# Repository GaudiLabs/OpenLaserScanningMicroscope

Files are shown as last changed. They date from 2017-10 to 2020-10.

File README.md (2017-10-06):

## OpenLaserScanningMicroscope 

Open Source Laser Scanning Microscope (OpenLSM)

### Don't click on the files!
Click on the "Download ZIP" Button to the right.
Then unpack the archive.

### Open Source Digital Microfluidics Bio Lab

OpenLSM is an open source design to build a laser scanning microscope from a DVD or Blue-Ray disc reading head. 

For more info on the open source project see:
http://www.gaudi.ch/GaudiLabs/?page_id=652

### License

OpenLSM, all design files and software are licensed under a GNU GENERAL PUBLIC LICENSE
See license file in the repository.

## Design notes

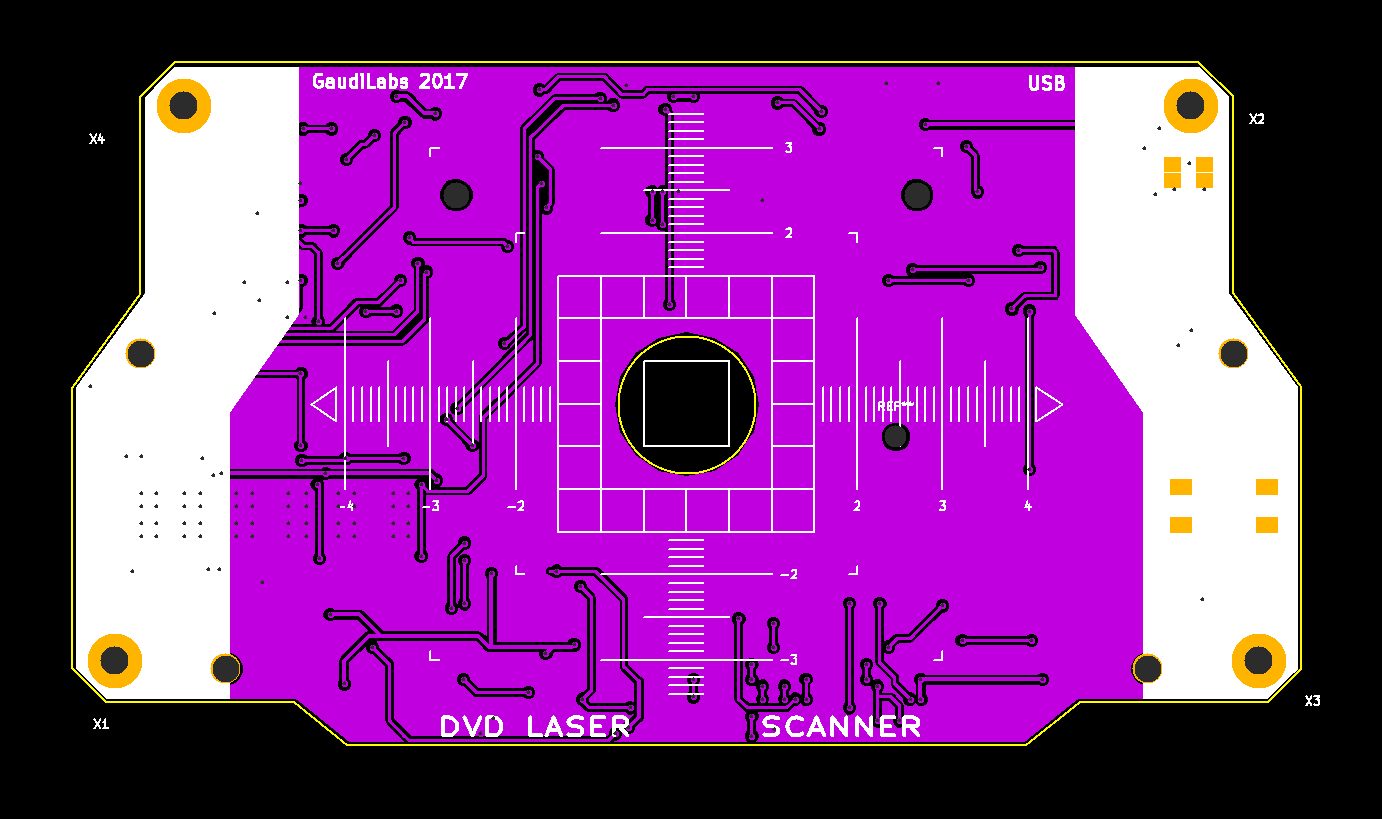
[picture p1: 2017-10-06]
PCB/DVDLaserScannerII/Pictures/DVDScannerII_Front.png

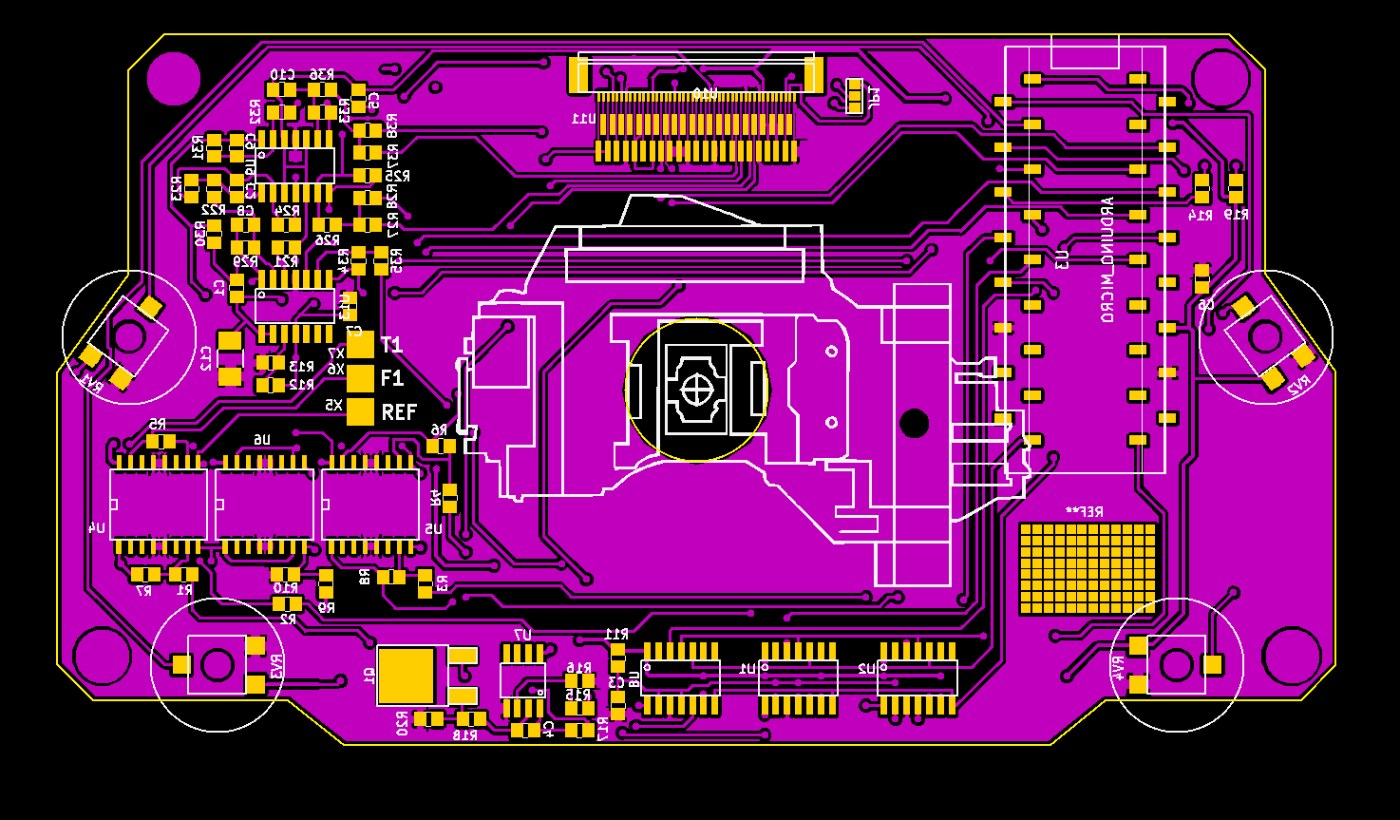
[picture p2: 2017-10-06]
PCB/DVDLaserScannerII/Pictures/DVDScanII.png

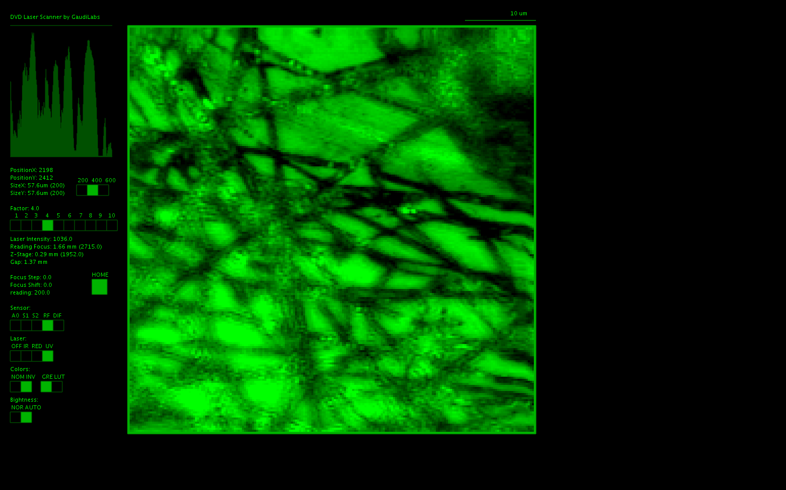
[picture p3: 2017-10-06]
ProcessingCode/DVDLaserV2_Inter/dump/LaserDump 2017-10-05 10:50:20.png

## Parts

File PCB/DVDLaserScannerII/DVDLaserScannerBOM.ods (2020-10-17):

Bill of Materials (BOM) DVD Laser Scanner V2
21. Juni 2017, Urs Gaudenz
Id | Quantity | Designator | Package | Order No | Designation | Quantity
26 | 3 | U4,U5,U6 | SO-16-W | 863-TCA0372DWG | TCA0372_DWG | 3
22 | 1 | U7 | SOIC-08_N |  | MCP6002 | 1
4 | 3 | U1,U2,U8 | SOIC-14_N |  | MCP4922-E/SL | 3
37 | 2 | U9,U13 | SOIC-14_N | 579-MCP6004-I/SL | MCP6004 | 2 | TLC2274
16 | 1 | Q1 | TO-252-2Lead | Q_NMOS_GDS | LR120N | 1
29 | 2 | C1,C8 | 0805G |  | 22pF | 2
30 | 2 | C2,C9 | 0805G | 33pF | 39pF | 2
7 | 1 | C3 | 0805G |  | 100nF | 1
14 | 3 | C4,C6,C7 | 0805G |  | 100nF | 3
31 | 2 | C5,C10 | 0805G |  | 10pF | 2
36 | 1 | C12 | C_1210_HandSoldering | ? 220 | 100nF | 1 |  | 470pF
15 | 2 | D1,D2 | 0805G |  | LED | 2 |  | 10pF
 |  | R2,R4, |  |  | 270k |  |  | 68pF
8 | 4 | R1,R3,R5,R6 | 0805G |  | 15k | 4 |  | 1nF
12 | 1 | R11 | 0805G |  | 100k | 1 |  | 2.2nF
13 | 1 | R13 | 0805G |  | 3.3k | 1 |  | 6.8nF
17 | 2 | R14,R19 | 0805G |  | 560 | 2 |  | 220nF
18 | 1 | R16 | 0805G |  | 1.8k | 1
19 | 1 | R17 | 0805G |  | 100 | 1 |  | 68Ohm
20 | 3 | R18,R22,R30 | 0805G |  | 10k | 3 |  | 8.2k
9 | 4 | R26,R36 | 0805G |  | 56k | 4 |  | 15k
21 | 1 | R20 | 0805G |  | 10 | 1 |  | 150k
25 | 2 | R21,R29 | 0805G |  | 39k | 2 |  | 180k
32 | 2 | R23,R31 | 0805G |  | 220k | 2 |  | 220k
33 | 2 | R24,R32 | 0805G |  | 68k | 2
34 | 2 | R25,R33 | 0805G |  | 18k | 2
35 | 4 | R27,R28,R37,R38 | 0805G |  | 1.2k | 4
10 | 3 | R7,R8,R15 | 0805G |  | 8.2k | 3
11 | 3 | R9,R10,R12 | 0805G |  | 4.7k | 5
 | 1 | R34 |  |  | 560k
 | 1 | R35 |  |  | 2.7k
5 | 1 | U3 | ARDUINO_MICRO_SMD |  | ARDUINO_MICRO | 1
3 | 4 | RV4,RV3,RV2,RV1 | CA6_VSMD | CA6 Carbon Potentiometers CA | ACP 6-SMD 10K | 4
3 |  |  |  | Poti Pins
2 | 1 | U11 | FFC_05_45 | 798-FH12A-45S0.5SH55 | Con45 | 1
 | 1 |  | FCC Cable | 710-687645152002 |  | 1
28 | 1 | SW1 | PUSH_BUTTON_SMD |  | BUT | 1
 | 2 |  | DVD Head | ebay | PHR-803T | 2
 | 1 |  | Mounting Brackets |  |  | 1
 | 1 |  | Mounting Brackets |  |  | 1
 | 4 |  | Spacers |  |  | 4

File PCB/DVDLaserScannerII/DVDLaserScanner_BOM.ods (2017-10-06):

Id | Designator | Package | Quantity | Designation | Supplier and ref
2 | U1,U2,U8 | SOIC-14_N | 3 | MCP4922-E/SL
4 | U3 | ARDUINO_MICRO_SMD | 1 | ARDUINO_MICRO
5 | X1,X2,X3,X4 | MountingHoleM3 | 4 | MountPad3 |  | reichelt
6 | C1,C2 | FFC_05_24 | 2 | SF-HF65
7 | REF** | HeatSink19x13 | 1 | HeatSink19x13 |  | reichelt
8 | U4,U5,U6 | SOIC-08_N | 3 | TCA0372 | mouser
9 | C3 | 0805G | 1 | 100nF
10 | R1,R3,R5,R6 | 0805G | 4 | 15k
11 | R2,R4 | 0805G | 2 | 56k
12 | R7,R8,R15 | 0805G | 3 | 8.2k
13 | R9,R10,R12 | 0805G | 3 | 4.7k
14 | R11 | 0805G | 1 | 100k
15 | R13 | 0805G | 1 | 3.3k
16 | C4 | 0805G | 1 | 100n | 1nF?
17 | D1,D2 | 0805G | 2 | LED
18 | Q1 | TO-252-2Lead | 1 | Q_NMOS_GDS
19 | R14,R19 | 0805G | 2 | 470
20 | R16 | 0805G | 1 | 1.8k
21 | R17 | 0805G | 1 | 100
22 | R18 | 0805G | 1 | 10k
23 | R20 | 0805G | 1 | 10
24 | U7 | SOIC-08_N | 1 | MCP6002
25 | U9 | Pads_24 | 1 | Con24 | mouser
26 | U11 | FFC_05_45 | 1 | Con45 | mouser
27 | U10 | Pads | 1 | Con45 | mouser
30 | R21 | 0805G | 1 | 2.2k
31 | RV4,RV3,RV2,RV1 | CA6_VSMD | 4 | POT |  | reichelt

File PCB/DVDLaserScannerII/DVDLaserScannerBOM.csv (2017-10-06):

Id | Designator | Package | Quantity | Designation | Supplier and ref
1 | REF** | MicroscopeyScale | 1 | MicroscopeyScale
2 | U11 | FFC_05_45 | 1 | Con45
3 | RV4,RV3,RV2,RV1 | CA6_VSMD | 4 | POT
4 | U1,U2,U8 | SOIC-14_N | 3 | MCP4922-E/SL
5 | U3 | ARDUINO_MICRO_SMD | 1 | ARDUINO_MICRO
6 | X1,X2,X3,X4 | MountingHoleM3 | 4 | MountPad3
7 | C3 | 0805G | 1 | 100nF
8 | R1,R3,R5,R6 | 0805G | 4 | 15k
9 | R2,R4,R26,R36 | 0805G | 4 | 56k
10 | R7,R8,R15 | 0805G | 3 | 8.2k
11 | R9,R10,R12,R34,R35 | 0805G | 5 | 4.7k
12 | R11 | 0805G | 1 | 100k
13 | R13 | 0805G | 1 | 3.3k
14 | C4,C6,C7 | 0805G | 3 | 100n
15 | D1,D2 | 0805G | 2 | LED
16 | Q1 | TO-252-2Lead | 1 | Q_NMOS_GDS
17 | R14,R19 | 0805G | 2 | 470
18 | R16 | 0805G | 1 | 1.8k
19 | R17 | 0805G | 1 | 100
20 | R18,R22,R30 | 0805G | 3 | 10k
21 | R20 | 0805G | 1 | 10
22 | U7 | SOIC-08_N | 1 | MCP6002
23 | REF**,REF** | MountingHole_3mm | 2 | MountingHole_3mm
24 | JP1 | GS3 | 1 | Jumper_NC_Dual
25 | R21,R29 | 0805G | 2 | 39k
26 | U4,U5,U6 | SO-16-W | 3 | TCA0372_DWG
27 | U10 | Pads | 1 | Con45
28 | SW1 | PUSH_BUTTON_SMD | 1 | BUT
29 | C1,C8 | 0805G | 2 | 22pF
30 | C2,C9 | 0805G | 2 | 39pF
31 | C5,C10 | 0805G | 2 | 10pF
32 | R23,R31 | 0805G | 2 | 180k
33 | R24,R32 | 0805G | 2 | 68k
34 | R25,R33 | 0805G | 2 | 18k
35 | R27,R28,R37,R38 | 0805G | 4 | 1.2k
36 | C12 | C_1210_HandSoldering | 1 | CP_Small
37 | U9,U13 | SOIC-14_N | 2 | TLC2274
38 | G*** | PHR-803T | 1 | LOGO
39 | X5,X6,X7 | PAD_SMD_3mm | 3 | PAD
40 | REF** | MountingHole_2-5mm | 1 | MountingHole_2-5mm
41 | REF** | SMD_Array | 1 | SMD_Array

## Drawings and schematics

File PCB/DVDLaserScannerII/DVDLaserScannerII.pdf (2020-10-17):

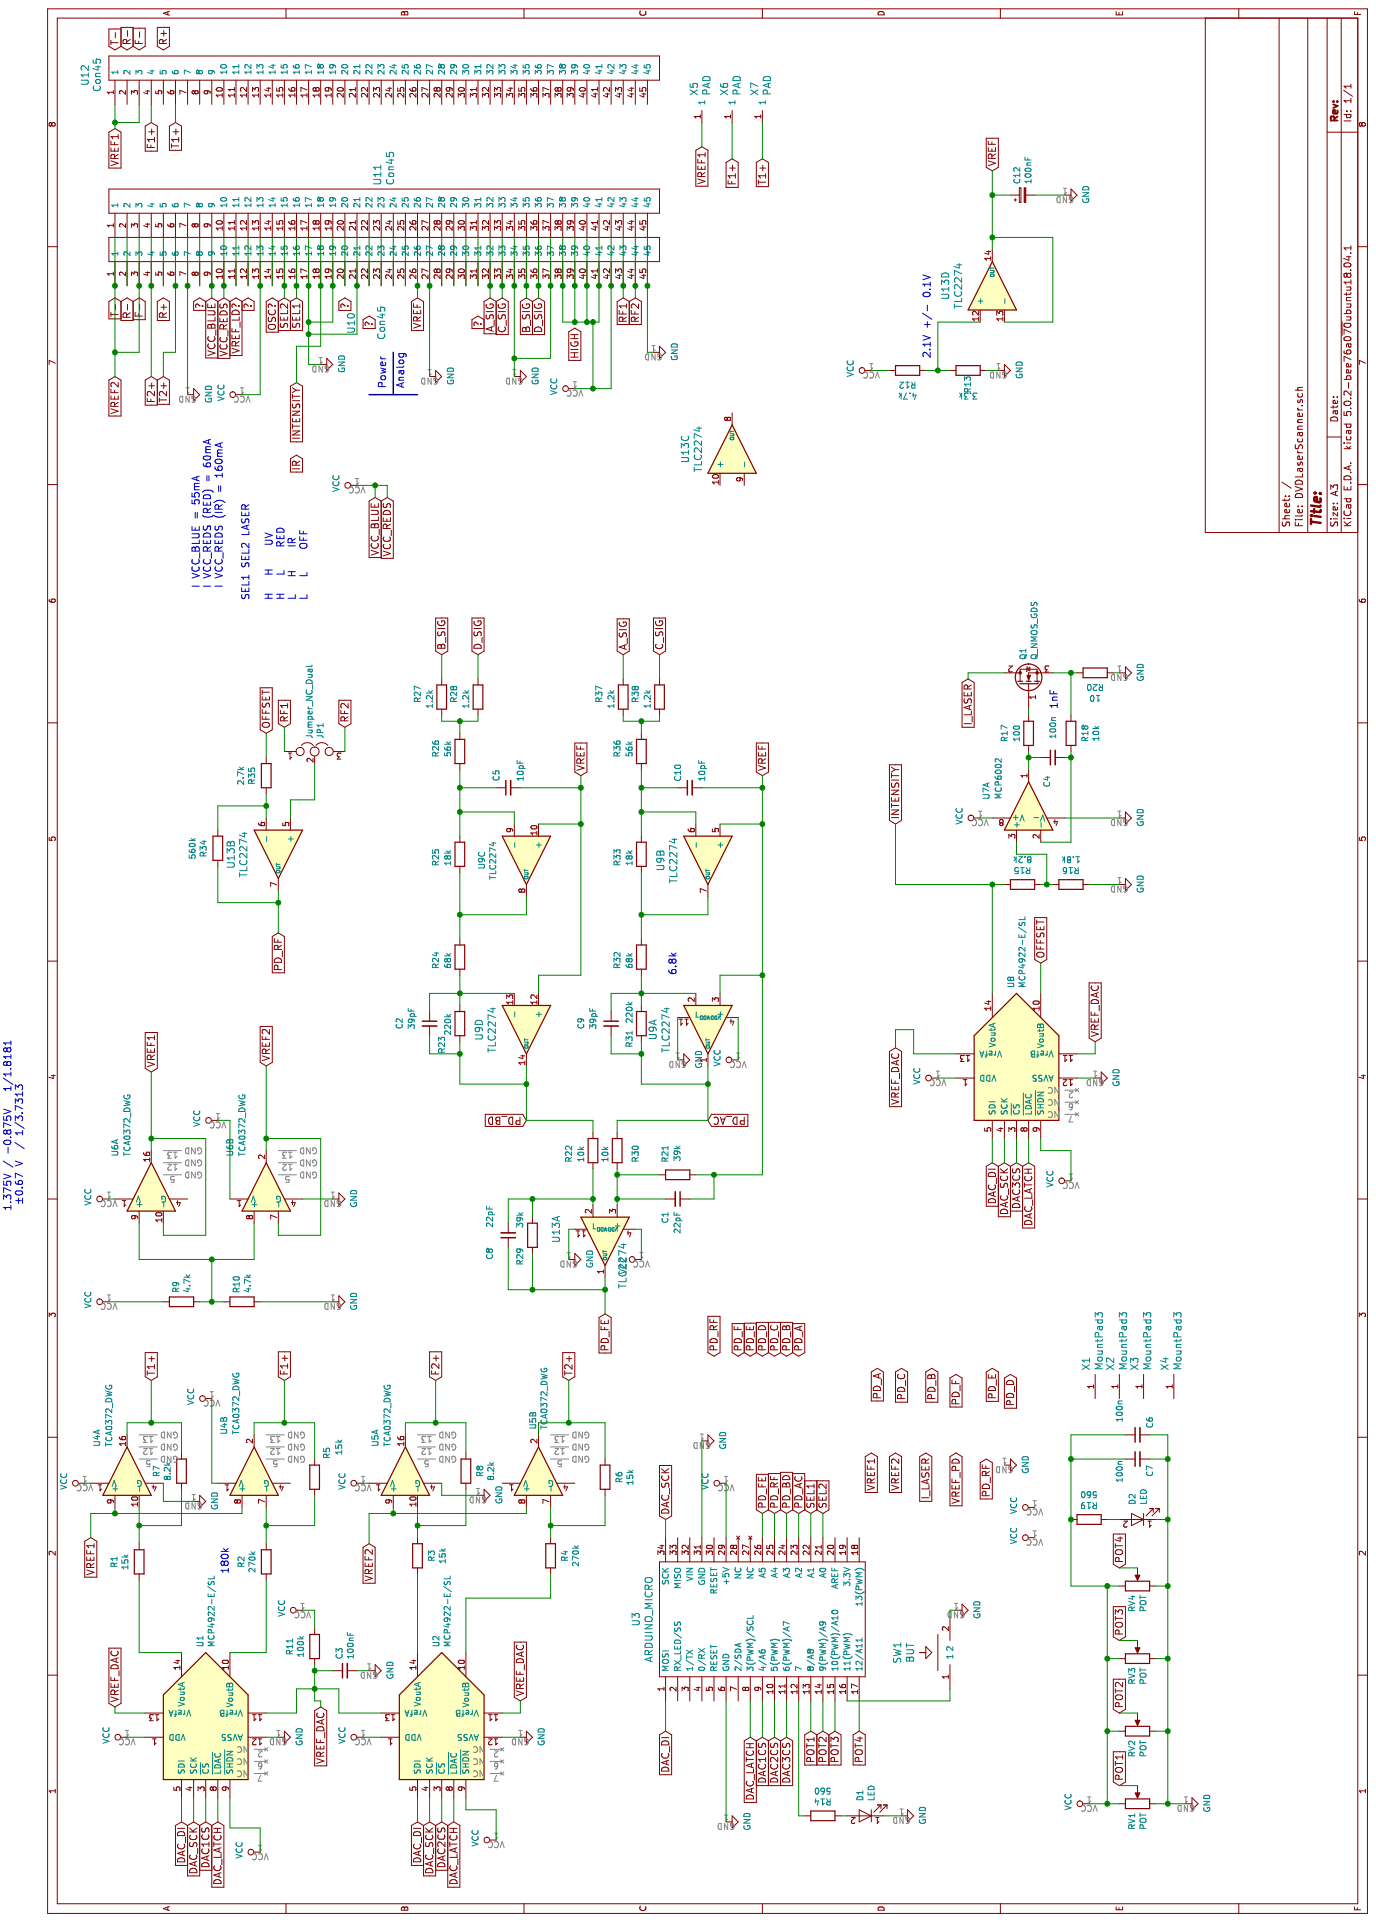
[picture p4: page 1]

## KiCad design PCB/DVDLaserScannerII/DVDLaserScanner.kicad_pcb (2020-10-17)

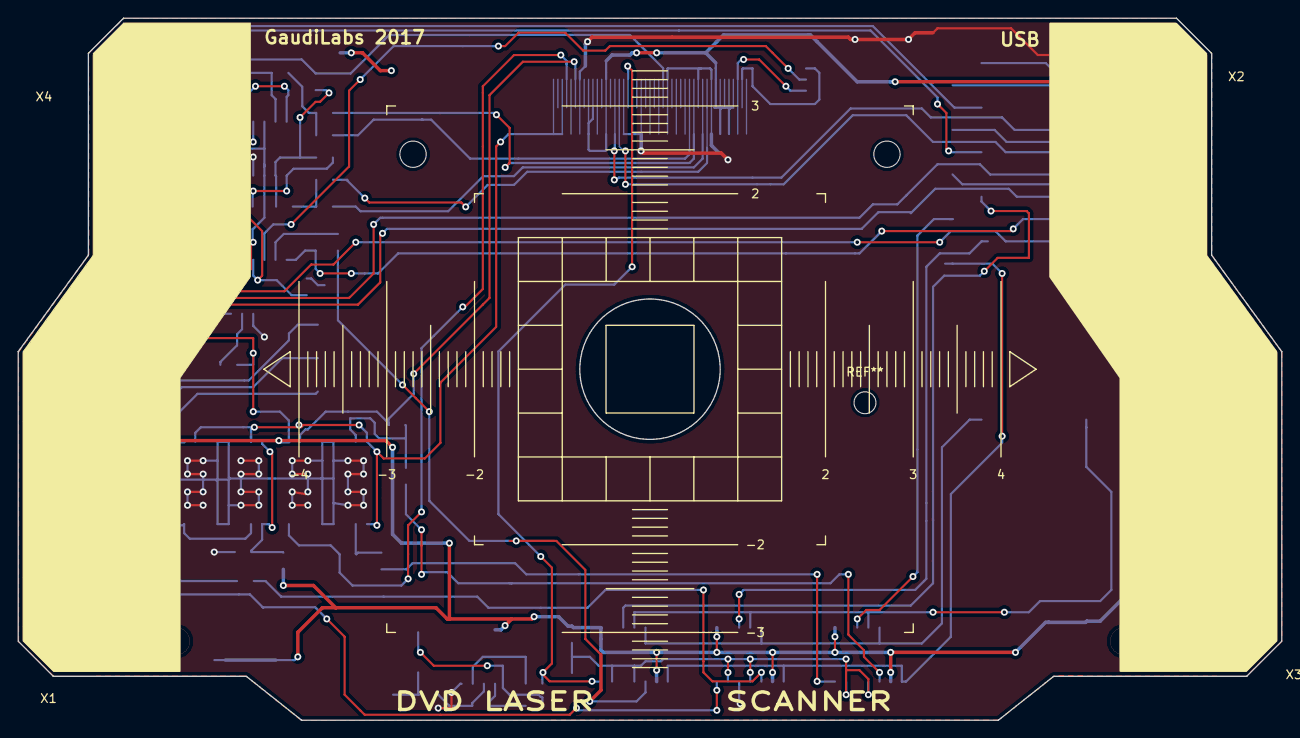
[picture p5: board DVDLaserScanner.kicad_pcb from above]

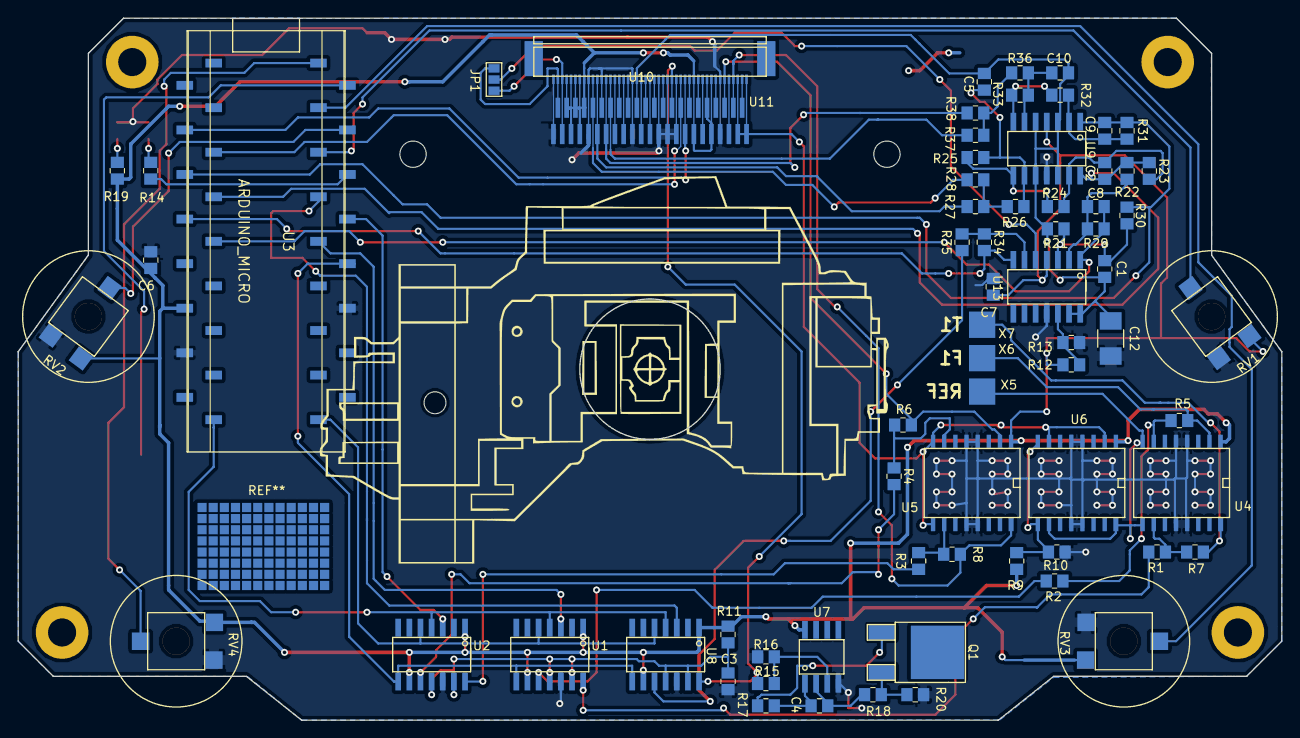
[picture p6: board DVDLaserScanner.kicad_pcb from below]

Board: 2 copper layers, 144.0 x 80.0 mm, 77 parts (70 on the bottom side), 80 nets.

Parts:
C1, C8: 22pF; 0805G
C2, C9: 39pF; 0805G
C3: 100nF; 0805G
C4, C6, C7: 100n; 0805G
C5, C10: 10pF; 0805G
C12: 100nF; C_1210_HandSoldering
D1, D2: LED; 0805G
JP1: Jumper_NC_Dual; GS3
Q1: Q_NMOS_GDS; TO-252-2Lead
R1, R3, R5, R6: 15k; 0805G
R2, R4: 270k; 0805G
R7, R8, R15: 8.2k; 0805G
R9, R10, R12: 4.7k; 0805G
R11: 100k; 0805G
R13: 3.3k; 0805G
R14, R19: 470; 0805G
R16: 1.8k; 0805G
R17: 100; 0805G
R18, R22, R30: 10k; 0805G
R20: 10; 0805G
R21, R29: 39k; 0805G
R23, R31: 180k; 0805G
R24, R32: 68k; 0805G
R25, R33: 18k; 0805G
R26, R36: 56k; 0805G
R27, R28, R37, R38: 1.2k; 0805G
R34: 560k; 0805G
R35: 2.7k; 0805G
RV1, RV2, RV3, RV4: POT; CA6_VSMD
SW1: BUT; PUSH_BUTTON_SMD
U1, U2, U8: MCP4922-E/SL; SOIC-14_N
U3: ARDUINO_MICRO; ARDUINO_MICRO_SMD
U4, U5, U6: TCA0372_DWG; SO-16-W
U7: MCP6002; SOIC-08_N
U9, U13: TLC2274; SOIC-14_N
U10: Con45; Pads
U11: Con45; FFC_05_45
X1, X2, X3, X4: MountPad3; MountingHoleM3
X5, X6, X7: PAD; PAD_SMD_3mm

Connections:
A_SIG: R37.1, U10.32, U11.32
B_SIG: R27.1, U10.35, U11.35
C_SIG: R38.1, U10.33, U11.33
DAC1CS: U1.3, U3.9
DAC2CS: U2.3, U3.10
DAC3CS: U3.11, U8.3
DAC_DI: U1.5, U2.5, U3.1, U8.5
DAC_LATCH: U1.8, U2.8, U3.8, U8.8
DAC_SCK: U1.4, U2.4, U3.34, U8.4
D_SIG: R28.1, U10.36, U11.36
F1+: R5.1, U4.2, X6.1
F2+: R8.1, U5.16, U10.4, U11.4
F-: U5.8, U5.9, U6.2, U6.7, U10.1, U10.3, U11.1, U11.3
GND: C3.2, C6.2, C7.2, C12.2, D1.1, D2.1, R10.2, R13.1, R16.2, R20.1, RV1.3, RV2.3, RV3.3, RV4.3, SW1.2, U1.12, U2.12, U3.6, U3.31, U4.4, U4.5, U4.12, U4.13, U5.4, U5.5, U5.12, U5.13, U6.4, U6.5, U6.12, U6.13, U7.4, U8.12, U9.11, U10.7, U10.17, U10.19, U10.21, U10.27, U10.34, U10.37, U10.45, U11.7, U11.17, U11.19, U11.21, U11.27, U11.34, U11.37, U11.45, U13.11
INTENSITY: R15.1, U8.14, U10.18, U11.18
unnamed: C1.2, R21.2, R30.2, U13.3
unnamed: C2.1, R23.1, R24.2, U9.13
unnamed: C4.1, R17.2, U7.1
unnamed: C4.2, R18.2, U7.2
unnamed: C5.1, R25.1, R26.2, U9.9
unnamed: C8.2, R22.2, R29.2, U13.2
unnamed: C9.1, R31.1, R32.2, U9.2
unnamed: C10.1, R33.1, R36.2, U9.6
unnamed: D1.2, R14.2
unnamed: D2.2, R19.2
unnamed: JP1.2, U13.5
unnamed: Q1.1, R17.1
unnamed: Q1.3, R18.1, R20.2
unnamed: R1.1, R7.2, U4.10
unnamed: R1.2, U1.14
unnamed: R2.1, R5.2, U4.7
unnamed: R2.2, U1.10
unnamed: R3.1, R8.2, U5.10
unnamed: R3.2, U2.14
unnamed: R4.1, R6.2, U5.7
unnamed: R4.2, U2.10
unnamed: R9.2, R10.1, U6.8, U6.9
unnamed: R12.1, R13.2, U13.12
unnamed: R14.1, U3.12
unnamed: R15.2, R16.1, U7.3
unnamed: R24.1, R25.2, U9.8
unnamed: R26.1, R27.2, R28.2
unnamed: R32.1, R33.2, U9.7
unnamed: R34.2, R35.1, U13.6
unnamed: R36.1, R37.2, R38.2
unnamed: SW1.1, U3.16
unnamed: U10.2, U11.2
unnamed: U10.5, U11.5
unnamed: U10.8, U11.8
unnamed: U10.11, U11.11
unnamed: U10.12, U11.12
unnamed: U10.14, U11.14
unnamed: U10.20, U11.20
unnamed: U10.22, U11.22
unnamed: U10.23, U11.23
unnamed: U10.24, U11.24
unnamed: U10.25, U11.25
unnamed: U10.28, U11.28
unnamed: U10.29, U11.29
unnamed: U10.30, U11.30
unnamed: U10.31, U11.31
OFFSET: R35.2, U8.10
PD_AC: C9.2, R30.1, R31.2, U3.23, U9.1
PD_BD: C2.2, R22.1, R23.2, U3.24, U9.14
PD_FE: C8.1, R29.1, U3.26, U13.1
PD_RF: R34.1, U3.25, U13.7
POT1: RV1.2, U3.13
POT2: RV2.2, U3.14
POT3: RV3.2, U3.15
POT4: RV4.2, U3.17
RF1: JP1.1, U10.43, U11.43
RF2: JP1.3, U10.44, U11.44
SEL1: U3.22, U10.16, U11.16
SEL2: U3.21, U10.15, U11.15
T1+: R7.1, U4.16, X7.1
T2+: R6.1, U5.2, U10.6, U11.6
VCC_BLUE: C6.1, C7.1, R9.1, R11.1, R12.2, R19.1, RV1.1, RV2.1, RV3.1, RV4.1, U1.1, U1.9, U2.1, U2.9, U3.29, U4.1, U5.1, U6.1, U7.8, U8.1, U8.9, U9.4, U10.9, U10.10, U10.13, U10.38, U10.39, U10.40, U10.41, U10.42, U11.9, U11.10, U11.13, U11.38, U11.39, U11.40, U11.41, U11.42, U13.4
VREF: C1.1, C5.2, C10.2, C12.1, R21.1, U9.3, U9.5, U9.10, U9.12, U10.26, U11.26, U13.13, U13.14
VREF1: U4.8, U4.9, U6.10, U6.16, X5.1
VREF_DAC: C3.1, R11.2, U1.11, U1.13, U2.11, U2.13, U8.11, U8.13

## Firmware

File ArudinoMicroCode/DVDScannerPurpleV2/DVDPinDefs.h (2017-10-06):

/**
 * \file
 * Pin definitions
 */



//------------------------------------------------------------------------------
// DAC pin definitions

// LDAC may be connected to ground to save a pin
/** Set USE_MCP_DAC_LDAC to 0 if LDAC is grounded. */
#define USE_MCP_DAC_LDAC 1

// use arduino pins 2, 3, 4, 5 for DAC

// pin 2 is DAC chip select

/** Data direction register for DAC chip select. */
#define MCP_DAC1_CS_DDR DDRD
#define MCP_DAC2_CS_DDR DDRC
#define MCP_DAC3_CS_DDR DDRD

/** Port register for DAC chip select. */
#define MCP_DAC1_CS_PORT PORTD
#define MCP_DAC2_CS_PORT PORTC
#define MCP_DAC3_CS_PORT PORTD

/** Port bit number for DAC chip select. */
#define MCP_DAC1_CS_BIT 4
#define MCP_DAC2_CS_BIT 6
#define MCP_DAC3_CS_BIT 7

// pin 3 is DAC serial clock
/** Data direction register for DAC clock. */
#define MCP_DAC_SCK_DDR DDRB
/** Port register for DAC clock. */
#define MCP_DAC_SCK_PORT PORTB
/** Port bit number for DAC clock. */
#define MCP_DAC_SCK_BIT 1

// pin 4 is DAC serial data in

/** Data direction register for DAC serial in. */
#define MCP_DAC_SDI_DDR  DDRB
/** Port register for DAC clock. */
#define MCP_DAC_SDI_PORT PORTB
/** Port bit number for DAC clock. */
#define MCP_DAC_SDI_BIT  2

// pin 5 is LDAC if used
#if USE_MCP_DAC_LDAC
/** Data direction register for Latch DAC Input. */
#define MCP_DAC_LDAC_DDR  DDRD
/** Port register for Latch DAC Input. */
#define MCP_DAC_LDAC_PORT PORTD
/** Port bit number for Latch DAC Input. */
#define MCP_DAC_LDAC_BIT  0
#endif // USE_MCP_DAC_LDAC

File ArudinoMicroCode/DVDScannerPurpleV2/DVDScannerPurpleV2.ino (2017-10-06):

/*
  Analog input, analog output, serial output

 Reads an analog input pin, maps the result to a range from 0 to 255
 and uses the result to set the pulsewidth modulation (PWM) of an output pin.
 Also prints the results to the serial monitor.

 The circuit:
 * potentiometer connected to analog pin 0.
   Center pin of the potentiometer goes to the analog pin.
   side pins of the potentiometer go to +5V and ground
 * LED connected from digital pin 9 to ground

 created 29 Dec. 2008
 modified 9 Apr 2012
 by Tom Igoe

 This example code is in the public domain.

 */

#include "DVDPinDefs.h"
#include "mcpDac.h"


// These constants won't change.  They're used to give names
// to the pins used:
const int potTopLeft = A8;  // Analog input pin that the potentiometer is attached to
const int potTopRight = A9;  // Analog input pin that the potentiometer is attached to
const int potBottomLeft = A10;  // Analog input pin that the potentiometer is attached to
const int potBottomRight = A11;  // Analog input pin that the potentiometer is attached to

const int LEDPin = 7; // Analog output pin that the LED is attached to
const int buttonPin = 11;     // the number of the pushbutton pin


const int SEL2 =  A0;      // the number of the LED pin
const int SEL1 =  A1;      // the number of the LED pin
const int OSC =  2;      // the number of the LED pin


int potValue1,potValue2,potValue3,potValue4 = 0;        // value read from the pot
int potValueRaw1,potValueRaw2,potValueRaw3,potValueRaw4 = 0;        // value read from the pot

int outputValue = 1900;        // value output to the PWM (analog out)

int x=0;
int y=0;

 int sizeX=200;
 int sizeY=200;
 int posX=2170;
 int posY=2050;
 int fact=3;
 int chanel=5;

const int mode=0; //0: scanning xy  1:scanning xz
 int focus_shift=0;
const int focus_step=0;
const int csize=10;
float bounce_fact;

int control_data_in[csize*2];
int control_data_out[csize];


int intensitiy;
int c,val;
int j=0; 

void setup() {
  // initialize serial communications at 9600 bps:
  Serial.begin(115200);
       mcpDacInit();

pinMode(A1, INPUT);           // set pin to input
//digitalWrite(A1, HIGH);       // turn on pullup resistors
  pinMode(LEDPin, OUTPUT);

  pinMode(OSC, OUTPUT);
  pinMode(SEL1, OUTPUT);
  pinMode(SEL2, OUTPUT);
digitalWrite(OSC, HIGH);       // ?
digitalWrite(SEL1, HIGH);       // SEL1/SEL2 HIGH= UV SEL1/SEL2 LOW = OFF
digitalWrite(SEL2, HIGH);       //  SEL1 HIGH / SEL2 LOW = RED, SEL1 LOW / SEL2 HIGH = IR

x=sizeX;

mcpDac3BSend (1675);//Set Amp Offset

}

void loop() {
  
  
  if (Serial.available()>0) 
{
    control_data_in[j] =Serial.read();
    j++;


}

 
if (j==(csize*2))
{
  j=0;

  control_data_out[0]=potValue1<<2;   //Laser Intensity
  control_data_out[1]=(potValue2<<2)+(potValue4>>2)+focus_shift;  //Drive reading head focus
  control_data_out[2]=potValue3<<2;   //Drive stage Z
  control_data_out[4]=fact;
  control_data_out[5]=focus_step;
  control_data_out[6]=focus_shift;
 control_data_out[7]=control_data_in[0]*256+control_data_in[1];
 control_data_out[8]=control_data_in[2]*256+control_data_in[3];

  sizeX=control_data_in[0]*256+control_data_in[1];
  sizeY=control_data_in[2]*256+control_data_in[3];
  posX=control_data_in[4]*256+control_data_in[5];
  posY=control_data_in[6]*256+control_data_in[7];
  fact=control_data_in[8]*256+control_data_in[9];
  chanel=control_data_in[10]*256+control_data_in[11];
  if (control_data_in[13]==1)  y=0;
  
  if (control_data_in[15]>1) digitalWrite(SEL1, HIGH);  else digitalWrite(SEL1, LOW);
  if ((control_data_in[15]%2) == 0) digitalWrite(SEL2, LOW); else digitalWrite(SEL2, HIGH);

  
  
  for (int i=0; i < csize; i++){
Serial.write(control_data_out[i]&0xff);
Serial.write(control_data_out[i]>>8); //analogRead(A0)
  }
  
  bounce_fact=sizeX/10000;
  
for (int i=0; i < sizeX; i++)
  {
    x=(100-i)*(100-i)*bounce_fact;
     mcpDac2BSend(posX+((-(sizeX/2)+x)*fact));        //Drive reading head X
     delayMicroseconds(400);
  };
     delayMicroseconds(1000);


  x=0;
  y++;
    if (y>sizeY) {y=0;  focus_shift+=focus_step;}

 
}

  
  
if(x<sizeX)
{
  
  intensitiy = analogRead(A0+chanel);
  if (intensitiy<350) digitalWrite(LEDPin, HIGH); else digitalWrite(LEDPin, LOW);
     
   mcpDac2BSend(posX+((-(sizeX/2)+x)*fact));        //Drive reading head X

  if (mode==0) mcpDac1BSend(posY+((-(sizeY/2)+y)*fact));        //Drive stage Y
  if (mode==1) mcpDac2ASend(4096-y*20);  
   
x++;

Serial.write(intensitiy&0xff);
Serial.write(intensitiy>>8); //analogRead(A0)
 // digitalWrite(13, HIGH);   // turn the LED on (HIGH is the voltage level)
 // digitalWrite(13, LOW);    // turn the LED off by making the voltage LOW
 // delay(5);              // wait for a second
}


  
  
  
  // read the analog in value:
  potValueRaw1 = analogRead(potTopRight);
  potValueRaw2 = analogRead(potTopLeft);
  potValueRaw3 = analogRead(potBottomLeft);
  potValueRaw4 = analogRead(potBottomRight);

  if ((potValueRaw1-potValue1)>2) {potValue1=potValueRaw1-2;} // add hysteresis
  if ((potValue1-potValueRaw1)>2) {potValue1=potValueRaw1+2;}

  if ((potValueRaw2-potValue2)>2) {potValue2=potValueRaw2-2;}
  if ((potValue2-potValueRaw2)>2) {potValue2=potValueRaw2+2;}
  
  if ((potValueRaw3-potValue3)>2) {potValue3=potValueRaw3-2;}
  if ((potValue3-potValueRaw3)>2) {potValue3=potValueRaw3+2;}
  
  if ((potValueRaw4-potValue4)>2) {potValue4=potValueRaw4-2;}
  if ((potValue4-potValueRaw4)>2) {potValue4=potValueRaw4+2;}

  // map it to the range of the analog out:
 // outputValue = map(potValue, 0, 1023, 0, 4095);
  // change the analog out value:

  // print the results to the serial monitor:



  
  if (mode==0)  mcpDac2ASend((potValue2<<2)+(potValue4>>2)+focus_shift);        //Drive reading head focus
   //  mcpDac2ASend(outputValue);        //Drive reading head focus

   mcpDac1ASend(potValue3<<2);        //Drive stage Z


   mcpDac3ASend(potValue1<<2);        //Current for Laser Diode



  // wait+ 2 milliseconds before the next loop
  // for the analog-to-digital converter to settle
  // after the last reading:
     delayMicroseconds(1000);
}

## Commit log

2017-10-06 Added PCB files, Arduino and Processing code first online
    [DVDLaserScanner-B.Cu.gbr, DVDLaserScanner-B.Mask.gbr, DVDLaserScanner-B.Paste.gbr, DVDLaserScanner-B.SilkS.gbr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]
2020-10-17 Finally fixed error on U9 / U13 and updated BOM
    [DVDLaserScanner-2020-10-17-11-37-23.sch, DVDLaserScanner-2020-10-17-11-39-27.sch, DVDLaserScanner-B.Cu.gbr, DVDLaserScanner-B.Mask.gbr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]
2020-10-17 Updated Schematic PDF
    [DVDLaserScanner.sch, _saved_DVDLaserScanner.sch]
